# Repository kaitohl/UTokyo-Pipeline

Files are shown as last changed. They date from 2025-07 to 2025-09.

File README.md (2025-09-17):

# UTokyo-Pipeline

- Checkerboard folder contains images of the checkerboard used for calibration.
- STL Files folder contains STL file of the cluster and stereoscope camera and the camera holder.

# Term Translation

base2gripper = optical origin to cluster

gripper2cam = clubster to stereoscope camera

base2world = optical origin to checkerboard world space

world2cam = checker world space to stereoscop camera

## 1. Collection

- Collected 10-20 images with the stereoscope of a checkerboard with known square size. Hand-eye calibration can use the same image for calibration, so motion capture data was collected at the same time to create a paired dataset.
- Make sure to move the camera in different poses when capturing images and motion caputre data.
- Recommend to use a digital screen to display a checkerboard. This way you can percisely create a checkerboard.
- Square size used in this experiment was 10.0006 mm.

## 2. Split Images

- A single image capture with the stereoscope encodes both left and right images together.
- Split a single image by even and odd rows and determine which are left and right images.
- splitimages.ipynb was used to split scope images and organize mocap data.

## 3. Resizing

- After splitting an image to left and right images, the original number of rows will be cut in half.
- Need to upscale or downscale left and right images to desired resolution.
- Tested nearest neighbour (NN), bilinear interpolation (BL), bicubic interpolation (BC), Lanczos (LZ).

## 4. Calibrate Camera

- Use images collected and calibrate the camera.
- Check reprojection error to determine if calibration was good.
- Compared different calibration reprojection errors with different image sizes.
- workflow1.m in MATLAB was used to perform stereo calibration. Output was formatted to feed into OpenCV.

NN 1280x720: 0.2544 px
NN 1920x1080: 0.3014 px
BL 1280x720: 0.1898 px
BL 1920x1080: 0.3003 px
BC 1280x720: 0.1895 px
BC 1920x1080: 0.3017 px
LZ 1280x720: 0.1895 px
LZ 1920x1080: 0.3019 px

- No significant difference, so nearest neighbour at 1280x720 resolution was chosen for the rest of the experiment.

## 5. Hand-eye Calibrate

- Used the same calibration image/mocap dataset as camera calibration.
- workflow2.ipynb processes the calibration images by rectifying, and finding camera extrinsics.
- Using stereoParams_handeye2.mat, we get a mean reprojection error from solvePnP of **0.15 pixels**. This indicates the estimated camera extrinsics were excellent.
- The next section of workflow2.ipynb process the mocap data. A 4x4 transformation matrix is extracted for every pose of the cluster on the stereo camera. The transformation matrix is gripper2base.
- **Main error came from creating the transformation matrix. Important to read in Motive data as INTRISIC rotations.**
- The next section of workflow2.ipynb performs hand-eye calibration.The Shah method for hand-eye calibration was used. The average RMS reprojection error was **8.95 pixels**. This was calculated by reprojecting the checkerboard points using the estimated hand-eye transformation and camera intrinsics/extrinsics.
- Another validation step was to check the loop closure error. The average RMS rotation error was **0.005 degrees** and the average RMS translation error was **1.31 mm**.
- Attached is a visualization of the detected corners and reprojected corners using the estimated hand-eye transformation with an error of **8.69 pixels**. See reprojex.png.

reprojex

## 6. Testing

- Collected a new dataset of checkerboard images and mocap data.
- Used workflow2.ipynb to process the images and mocap data.
- Mocap data captured the cluster in different poses on the stereo camera
- Mocap data also captured the tip of the forceps in 5 different positions, touching the checkerboard at different corners.
- The idea is to move the forceps tip from motion capture space, into checkerboard world space using the estimated hand-eye transformation.
- The error metric is the distance from the forceps tip to the corresponding checkerboard corner in world space.
- The average distance error between the predicted tip position and the corresponding checkerboard corner was **20.34 mm**.
- The large error is likely due to the inaccuracy of the tip location tracked by the motion capture system. The tip was tracked using pivot calibration; however, the tip is not very sharp causing the calibration to be inaccurate.
- The next steps would be to improve the accuracy of the tip location in motion capture space. This could be done by using a sharper tip, or using a different method to track the tip.

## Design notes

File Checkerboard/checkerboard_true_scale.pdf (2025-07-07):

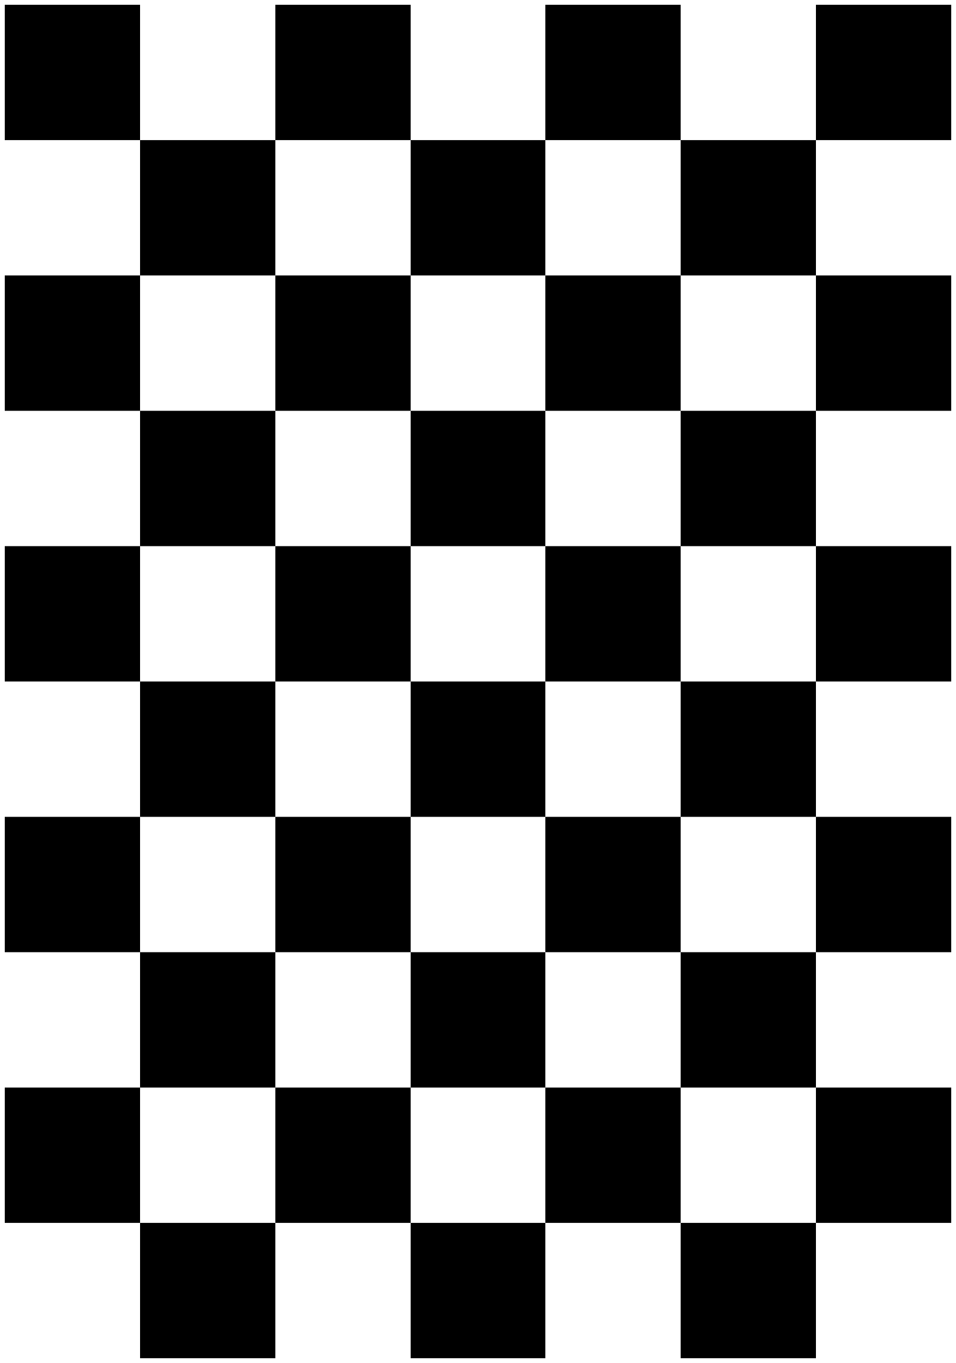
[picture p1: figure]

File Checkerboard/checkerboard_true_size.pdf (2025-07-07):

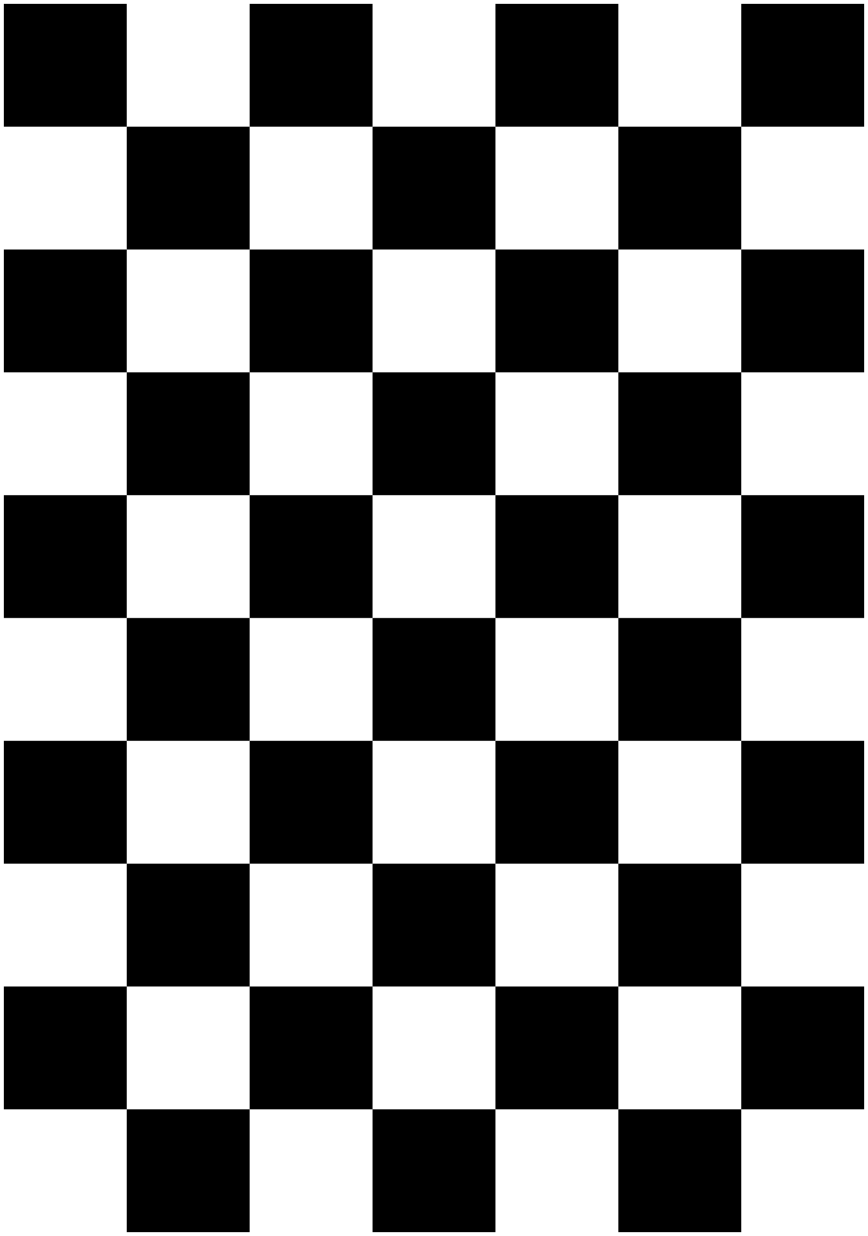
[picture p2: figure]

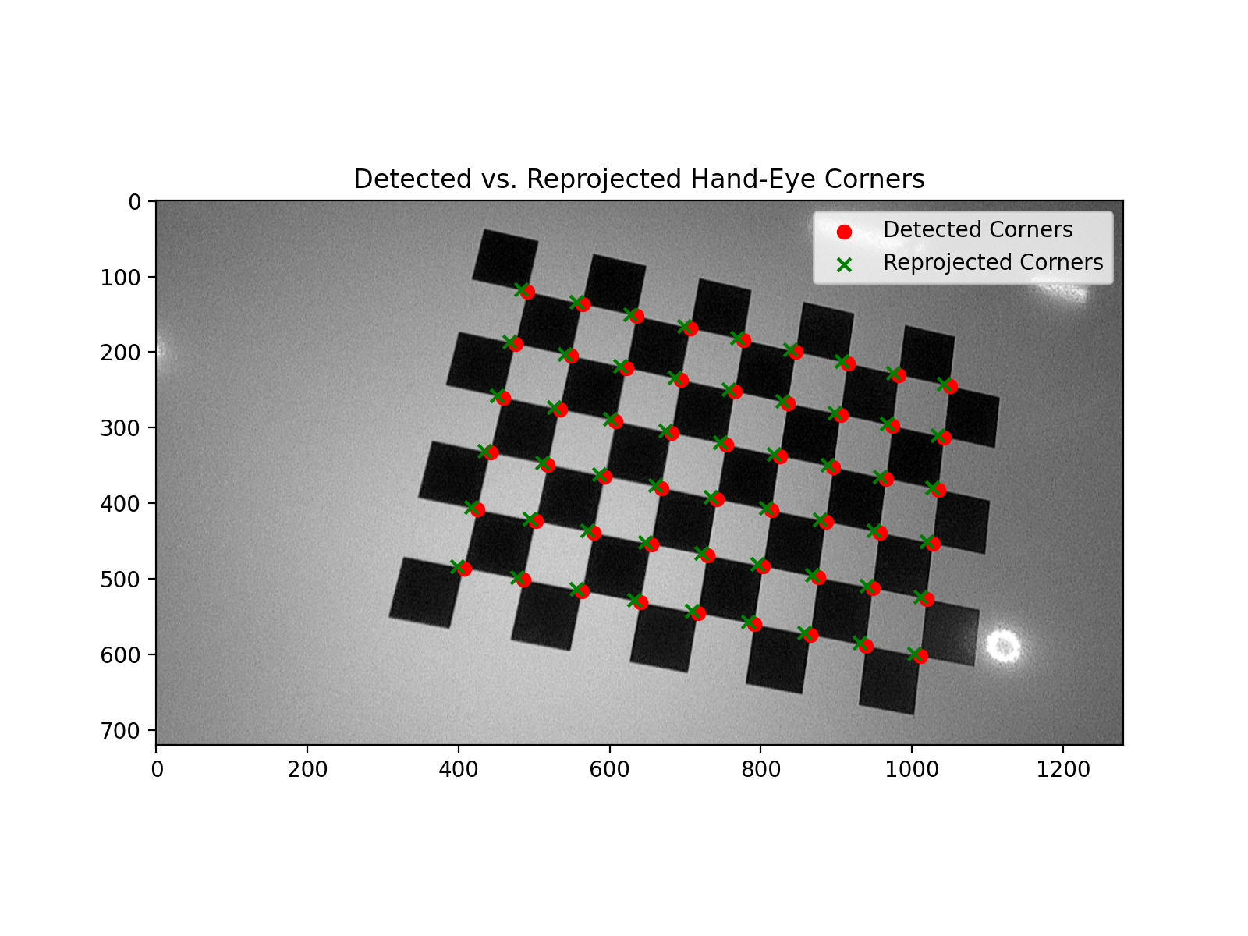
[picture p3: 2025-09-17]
reprojex.png

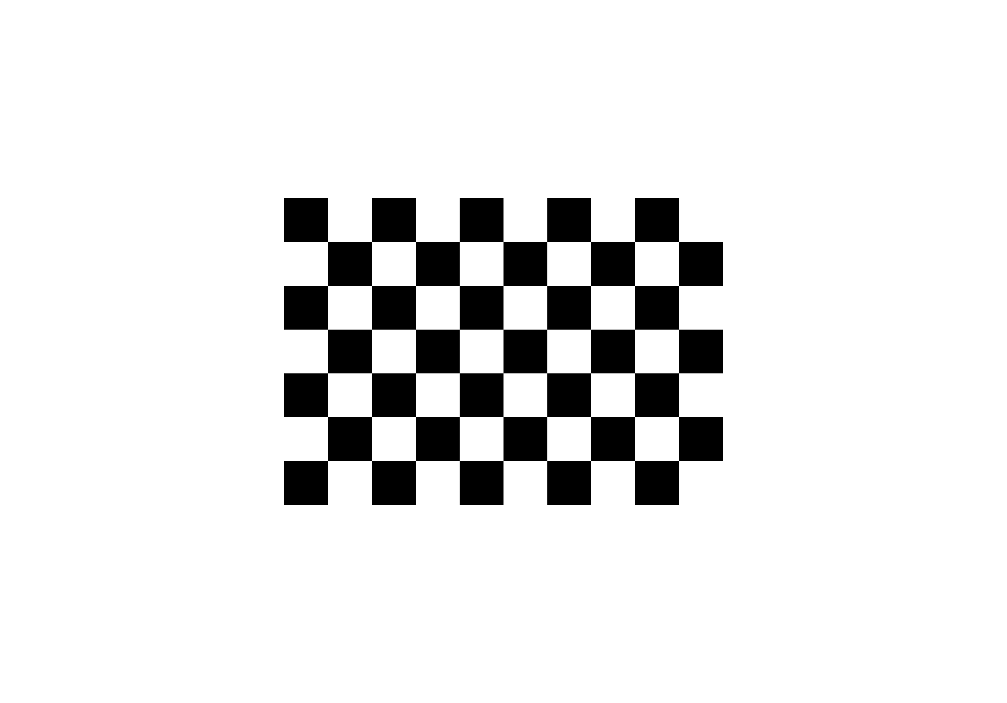
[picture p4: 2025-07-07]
Checkerboard/checkerboard_2388x1668.png

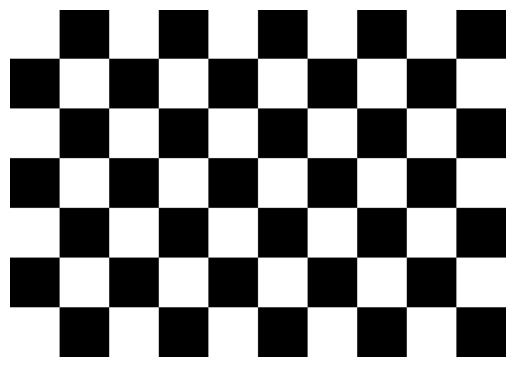
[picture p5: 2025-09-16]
Checkerboard/checker14mm.png

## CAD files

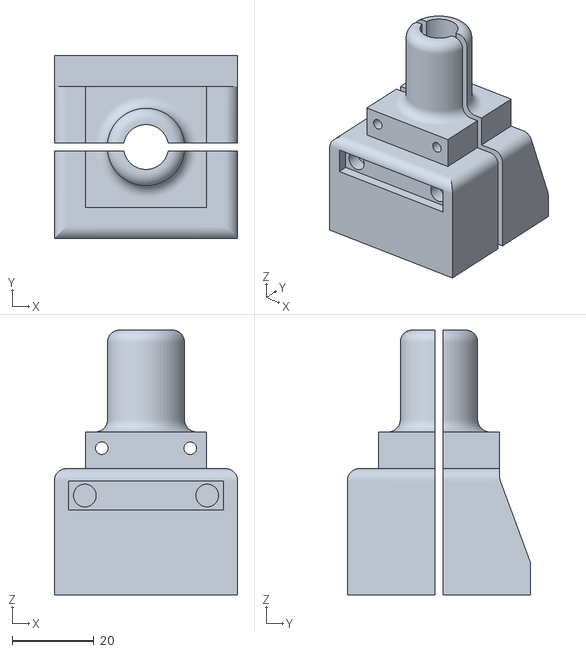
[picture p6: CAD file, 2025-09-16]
STL Files/split scope holder v3.stl
45.0 x 45.0 x 65.0

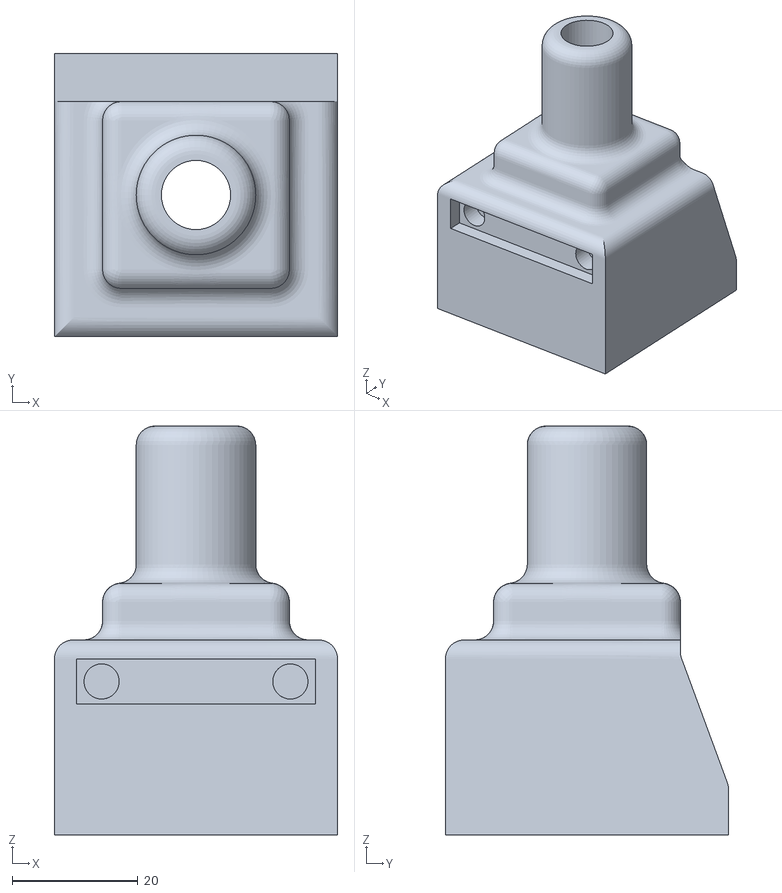
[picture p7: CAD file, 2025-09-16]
STL Files/scope holder v3.stl
45.0 x 45.0 x 65.0

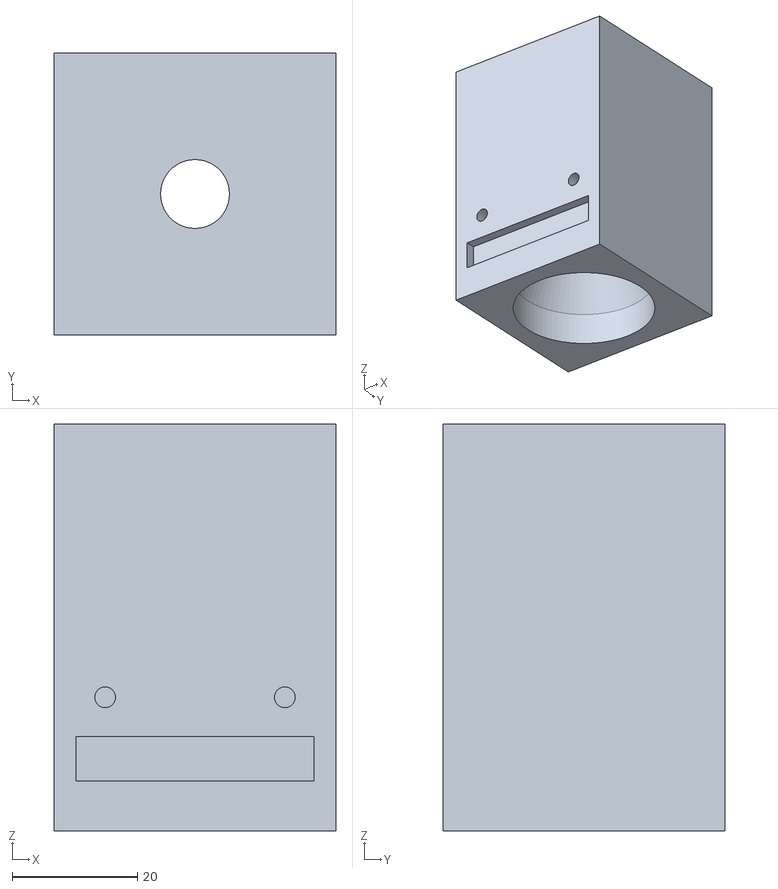
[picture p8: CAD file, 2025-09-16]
STL Files/scope holder v1.stl
45.0 x 45.0 x 65.0

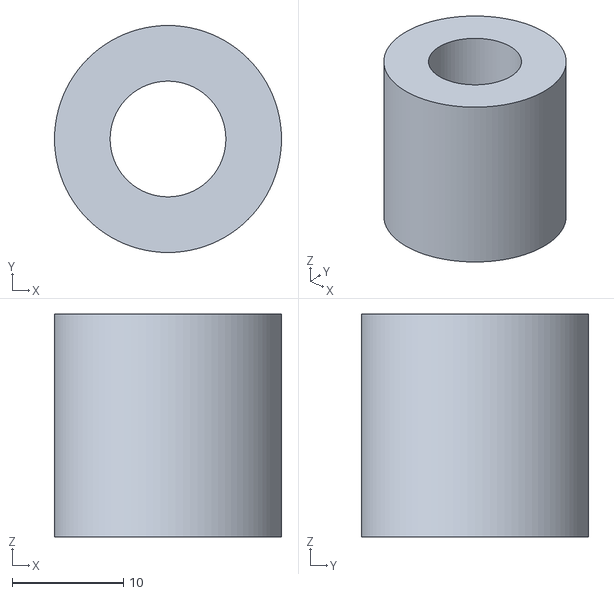
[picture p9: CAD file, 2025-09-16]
STL Files/testring01.stl
20.4 x 20.4 x 20.0

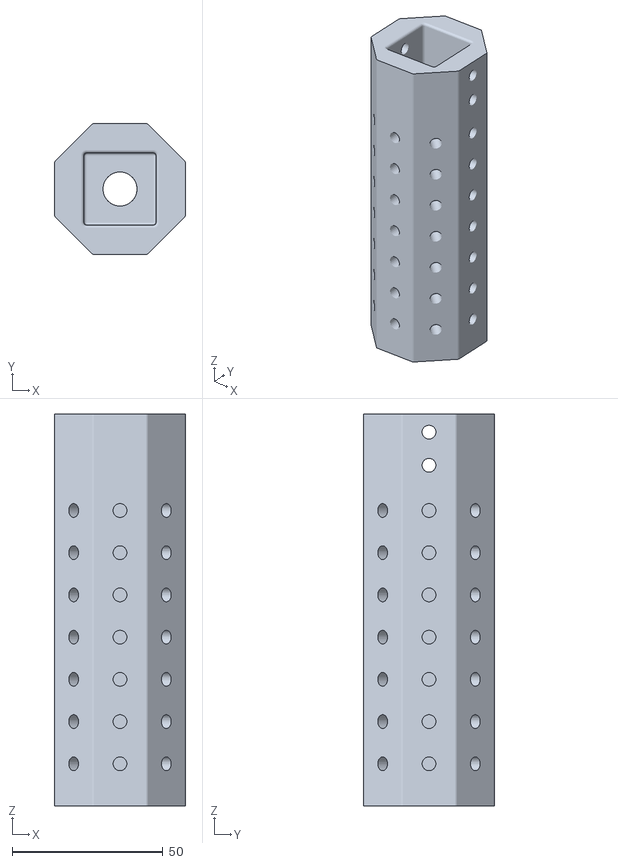
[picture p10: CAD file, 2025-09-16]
STL Files/marker v3.stl
43.5 x 43.5 x 130.0

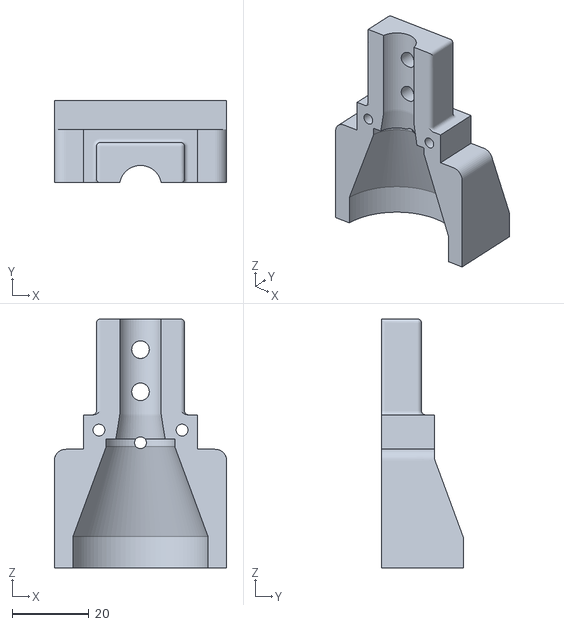
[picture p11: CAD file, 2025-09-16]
STL Files/upper scope holder v5.stl
45.0 x 21.5 x 65.0

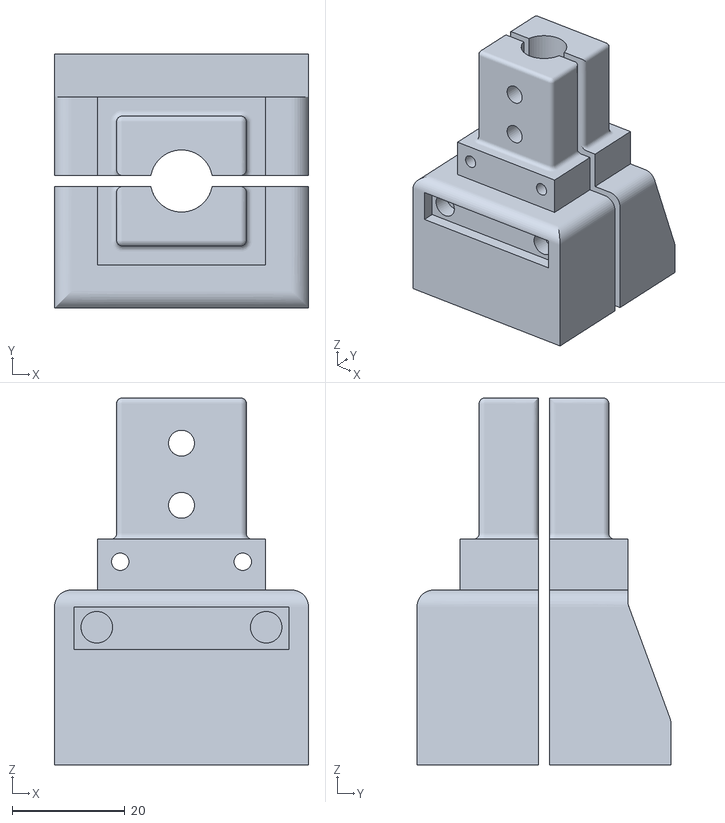
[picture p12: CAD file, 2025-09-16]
STL Files/upper scope holder v7.stl
45.0 x 45.0 x 65.0

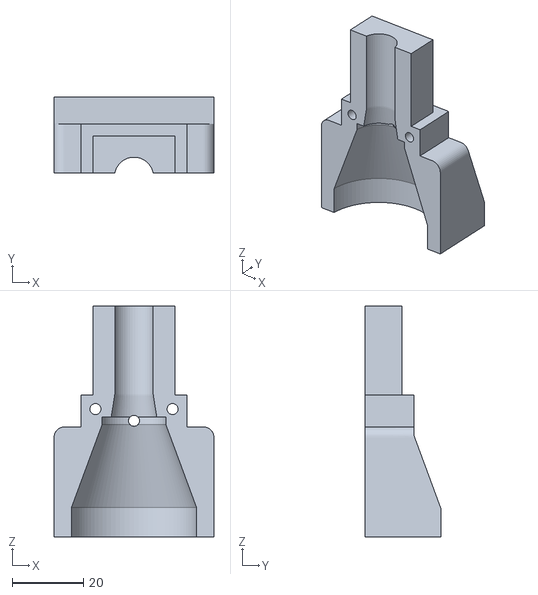
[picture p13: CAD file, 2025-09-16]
STL Files/upper scope holder v3.stl
45.0 x 21.5 x 65.0

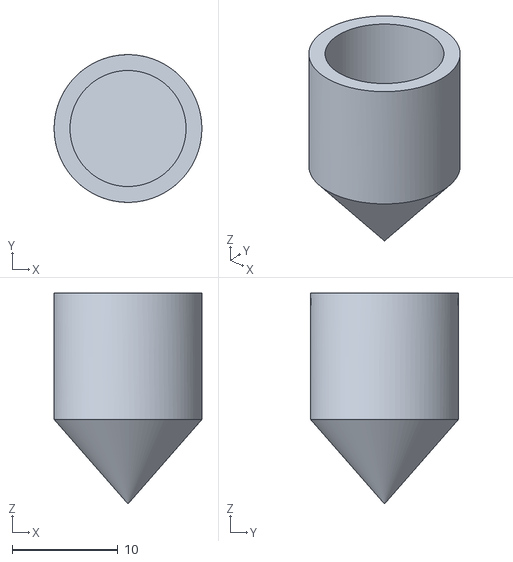
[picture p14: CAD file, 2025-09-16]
STL Files/Tipholder v1.stl
14.0 x 14.0 x 20.0

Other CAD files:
STL Files/split scope holder v2.stl
STL Files/marker v2.stl

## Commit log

2025-09-16 stl files
    [Tipholder v1.stl, marker v2.stl, marker v3.stl, scope holder v1.stl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]
2025-09-17 Update README with hand-eye calibration results
